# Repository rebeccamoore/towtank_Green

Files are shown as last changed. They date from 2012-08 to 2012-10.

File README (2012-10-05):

Section 1: An Introduction

This document serves as a comprehensive instruction manual for using the large tow-tank system in Link 280 at Syracuse University.  In this document, you will find descriptions of hardware and software.  It is the goal to establish this using some type of revision software.  The original document was maintained on github @ github.com/johndannenhoffer.

1.1: Document use

This document serves as a simple instruction manual for using the large tow-tank system in Link 280 at Syracuse University.  This was originally prepared by John Dannenhoffer IV.  To make changes, please indicate your name and contact information in the authors list (below) and specify which sections you contributed (and at what time these contributions were made).  If you have any questions regarding material, please direct your questions towards the most recent author of a section.  

1.1.2: Comments and plans for revision
Comments or plans for revisions will be presented using c-style comments.  This means that lines are commented using "//" and whole blocks of comments are denoted using a leading "/*" and a trailing "*/"

E.G.
This is a fake section to show commenting conventions used in this document.
//If you would like to commend a line, do so like this.

This is a list of things that will change over time.  So far we have…
foo
bar
foobar
/* this is something I plan to add later and finalize, but isn't currently finished yet
This is also something that should be continued */

1.1.3: Revision control software

By using revision control software, a document that goes through a number of changes can be maintained such that if undesirable changes are made, one can go back to previous versions.  Also, size is reduced by not having to keep archived files.  A free and easy to use software that implements revision control is Git and it's website github.com.  NOTE: To be free, an accounts material must remain open to the public.  This may be undesirable in the future.  There are two ways to use this software.  You can either download git to your local computer and manage your files (called repositories) that way or you can upload and download content through the web while logged into your account.

Branching: To change a document for your own purposes, create a branch from some node of the project.  Go to github.com to learn about this process.

Section 1.2 Authors

John Dannenhoffer IV (JFD4)
315-256-3521
johndannenhoffer@gmail.com

Summer research student for the summer of 2012.  Original author

Revision History
8/20/2012 - Created document and added sections 1,2,3, and 4 (JFD4)
//10/6/2012 - Added pictures of hardware (JFD4)

Section 1.2: Contents

This document contains a number of sections which describe different parts of the system (hardware, software, instructions,...)

1. Introduction:  Describes the use and maintenance of this document and its contents.

2. Running the tow tank:  A quick how-to guide to operating the tow tank.

3. Tow tank hardware:  The main hardware components are explained here

4. Tow tank software. The software used to run and gather data from the tow tank is described here

/* To be added later
5. PIV.  The components used for flow visualization are described here

6. Beginning Electronics for Experimentalists: This serves as a guide to electronics for experimentalists, especially those not 

7. Instrumentation for Experimentalists: A brief description of instrumentation techniques useful for the experimentalist.  This and the next section are geared towards experimentalists working in fluid mechanics

8. Actuation for Experimentalists: A description of actuation techniques useful for the experimentalist.  Microcontrollers, DC Motors, solenoids, servos, LEDs, MOSFETs and H-Bridge drivers, amplifiers, and much more will be discussed.  This section, along with sections 5 can serve as a guide to designing actuation system for experimental use.

9. Electronics Fabrication for Experimentalist:  This section describes experiential knowledge on different techniques to setup electronic apparatus for use in a lab setting.  Breadboarding, prototyping, soldering, and PCB (printed circuit board) production are discussed.

10. Purchasing: Specific vendors and purchasing techniques for everything electronic are discussed here.  Take this section with a grain of salt, as the electronics landscape changes very quickly.

*/

Section 2: Running the tow tank

This section describes the basics of running the tow tank.

2.1: What is needed to run the tow tank?

To run the tow tank, the following is needed to run the tow tank.

-Arduino hardware.  An Arduino is a micro controller development board which is used for quick prototyping of embedded systems.  Digital and analog signals from hardware can interfaced with software written in an easy to write c-based language.  The Arduino board (there are a number of generations of boards with slight differences) has header pin outputs for almost all of its pins.  This allows the user to connect peripherals to the Arduino such a digital signals, analog signals, serial signals, power,…  The board that was used for the first generation of the tow tank was the Arduino Uno.  Also, because there is a large Arduino community, a number of open source hardware and software tools have been developed.  Supplementary hardware which are attached on top of an Arduino are called shields.  These can serve many purposes.  Also, a number of software libraries have been developed to do various things within software, such as numerical calculations, interfacing with certain hardware,…  This project uses one shield (below) and its corresponding library.

-Arduino Software.  This is software that is used to communicate between a computer and the micro controller development board (Arduino).  Go to http://arduino.cc/en/Main/Software to download the latests version of the software. The Arduino software contains three important things.  1) An IDE (integrated development environment) to write and compile code in. 2) Drivers to communicate with the Arduino.  This allows you to upload your code onto the board.  It also allows for serial communication. 3) A serial monitor.  This allows the user to monitor the serial communication between the Arduino hardware and the computer.  This can be used very effectively as a debugging tool.

-A power source.  You need a way to power the power electronics in the tow tank system.  An ATX power supply and breakout board is used for this purpose.

-Pololu motor driver shield.  This "shield" is used in order to allow an Arduino to switch large amounts of current on an off.  http://www.pololu.com/catalog/product/2502  .  This shield plugs into the Arduino on top (it will only fit one way).  Through the connections with the Arduino, the program running on the Arduino controls the hardware on the shield and through this hardware, can control large amounts of current.  We use this to drive the motors for the tow tank.

-Pololu motor driver shield library.  To control the motor driver shield, software needs to be written on the Arduino.  Because interfacing with the shield is not trivial, a software library has been developed to make interfacing with the shield easier.  This allows simple function calls in your code to control the shield.  Go to https://github.com/pololu/Dual-VNH5019-Motor-Shield to download the zip file (click the "zip" button next to the "http" button.   Unzip this file.  Move the folder "DualVNH5019MotorShield" to the appropriate folder which holds your Arduino libraries.  On a mac, the directory would be ~/Documents/Arduino/libraries/. On Windows, it would be My Documents\Arduino\libraries .  NOTE:  If this is the first library that you are adding, you may need to create the "libraries" folder in the appropriate place.  When you launch the Arduino application, and you click the "Sketch" drop down and "Import Libraries", you should see the DualVNH5019-Motor-Shield as an option.  If you click this, it should add the line #include "DualVNH5019-Motor-Shield.h" to the top of your code.

-(OPTIONAL) Direction control board.  To prevent the system from causing itself harm by running the carriage into one of the sides, a control board was developed which uses 2 limit switches to limit motion.  If a limit switch is pressed, the carriage is stopped from moving in the direction of that limit switch, but can still move in the opposite direction.  See section 3.2.5 for more information on this.

2.2.1: Steps to run the tow tank w/o direction control.

Below are step by step instructions for setting up and running the tow tank.

1) Power source.  Make sure the power source is working.  Plug the 24-pin connector from the ATX power supply into the distribution board (the header is polarized).  Plug the power supply into a wall outlet and turn it on.  The fan should turn on.  NOTE: If you are using a first generation power distribution board (REV 1.0), you will need to solder together the green wire with one of the black wires.  /*This is addressed in later revisions of the boards.*/

2) Check power.  If the fan turns on, check the voltage levels of each of the outputs.  The power supply will output 4 different levels: Ground (GND), 3.3 volts (3V3), 5 volts (5V), and 12 volts (12V).  Using a multimeter in voltage mode, press the black probe to any exposed metal on the ground rail (lines denote which terminal blocks (green things) and barrier strips (black things) belong to which rail).  I suggest pressing the black probe to one of the screws in a ground (GND) terminal block.  Then take the red probe and connect it to the different rails.  The meter should read out approximately 3.3, 5.0 and 12.0 volts.  The board allows for higher voltages to be achieved by "stacking."  Refer to Section 3.2.4 for more information of this.

3) If the power is working (the fan turns on and the voltage levels seems to be correct), connect power to the motor driver shield.  To do this, connect the 12V on the power distro to the VIN of the motor driver shield and the GND to the GND.  Do this using a wire with stripped ends and the terminal blocks.  A blue LED should turn on.

4) Connect the motor to channel 1 of the motor driver shield.  Connect the output of the motor (the gray cable) to a barrier strip.  The gray cable has two spade terminal outputs.  Connect these to the long barrier strip on different strips (not across from each other).  A barrier strip connects the two connections in the same row.  From the barrier strip, connect the motor to the motor shield using a cable with a spade terminal on one end and a stripped wire on the other end.  The positive motor connection (red) should be connected to the M1A terminal connection.  The negative motor connection (black) should be connected to the M1B terminal connection.

NOTE: Using "beep" mode on the multimeter checks to see if connections are made.  The multimeter will emit a beep if a short is detected between the two probes.  This is extremely useful for checking to see if connections are securely made.

Use the multimeter to check that the positive terminal of the motor is connected to the M1A terminal and the negative terminal of the motor is connected to the M1B terminal.

IMPORTANT NOTE: IN BEGINNING TESTING, IT IS IMPORTANT TO MAKE SURE THAT THE SYSTEM DOESN'T BREAK ITSELF.  THIS MEANS THAT YOU SHOULD HAVE YOUR HAND ON THE POWER SUPPLY SWITCH DURING TESTING AND IF THE CARRIAGE APPROACHES A SIDE, TURN OFF THE POWER.  THIS IS ADDRESSED LATER WITH THE USE OF DIRECTION LIMITING CIRCUITS AND LIMIT SWITCHES, BUT UNTIL THOSE ARE PUT IN THE SYSTEM, PROCEED WITH CAUTION.

5) Test the motor.  Open the sketch (programs in Arduino are called sketches) called demo.pde (could be called demo.ino based on your version of the Arduino software downloaded).  This is in the pololu library zip file.  Connect the Arduino to the computer via USB cable (a light should go on on the Arduino) and click the upload button in the Arduino IDE (any compiling errors should be trivial and easily addressable).

6) "Plug" the shield into the Arduino.  This should fit only one way.

7) When the sketch is done uploading to the board (the yellow RX LED will flash while code is being uploaded onto the board), the system should start moving in the manner implemented in demo.pde.  The default (if you don't change any of the code) is to go one direction for ~1 second, speeding up along the way.  Then slow down for ~1 second to 0.  Then do the same thing in the opposite direction.  The motor should then stop for ~4 seconds.  This will then repeat.

2.2.2 Steps for running the tow tank w/ direction control:

Once the operation of the system is verified w/o direction control, implement the direction control.  This uses the direction control boards (small ~5cmx~5cm boards with 2 relays and other components) and 2 limit switches.

The steps for doing this are basically the same, but with 1 difference.  The motor must be put in series with the direction control circuit.  The workings of this control circuit are described in section 3.2.? but the basic idea is that if a limit switch is depressed, the motor can not move in a direction that would damage the system.  

To do this, take the connection between M1A and the barrier strip and "insert" the direction control circuit in this connection.

The only connection that is different for this setup is the connection between M1A and the barrier strip.  The new connections should be as follows.

-The positive terminal on the barrier strip (red spade terminal) should be connected to the CON1 screw terminal on the direction control board.  
-The CON2 screw terminal should be connected to the M1A connection on the motor driver shield.  
-Connect 12V and Ground to the board's screw terminal power connections.  

The board will allow current to flow only if the connection to the limit switch is closed (connected).  The connections to the limit switches are one the 4x1 header pin on the direction control board.  The 1 and 2 pins control 1 direction and the 3 and 4 pins control the other direction.  The wiring for this connector is described in Section 3.2.5

This means that to move in both directions, both 1 and 2 as well as 3 and 4 should be shorted.  To test this (without connecting the limit switches), use some metal object to short pins 1 and 2 and pins 3 and 4 (NOTE: It is ok to short 2 and 3 as well).

One easy way to test this setup is to use some metal object and short pins 1 and 2 while running the demo program.  The carriage should move in one direction as expected, but not the other.  Then short 3 and 4 and the carriage should move in the other direction.

NOTE:  Because the direction control board uses electromechanical relays, you will hear a click when you either make or break a connection (between 1 and 2 or 3 and 4).  This is perfectly normal.  However, you should only hear one click and if you hear multiple clicks that continue, the connection between the pins to be shorted is wrong.  Placing a precision screwdriver or allan wrench in the gap is a good way to make sure that the connection is correct.

IF EVERYTHING FUNCTIONS AS EXPECTED, THE HARDWARE SHOULD ALL BE WORKING AND YOU CAN MOVE FORWARD WITH PROGRAMMING!!!

Section 3 : Tow Tank Hardware

3.1: Physical hardware

3.1.1: The tank

3.1.2: Water containment

3.2: Electronic Hardware

3.2.1: Motor

3.2.2: Motor tachometer

3.2.3: Carriage Tachometer

3.2.4: Power distribution board

3.2.5: Direction Control Board

3.2.6: Arduino

3.2.7: Pololu Motor Driver Shield

3.2.8: Level Shifter

Section 4 : Tow Tank Software

4.1: Control software

4.1.1: Arduino

4.1.2: Pololu Motor Driver Shield Library

4.1.3: Level shifter arduino library

4.1.4: Test programs

4.1.5: Serial GUI

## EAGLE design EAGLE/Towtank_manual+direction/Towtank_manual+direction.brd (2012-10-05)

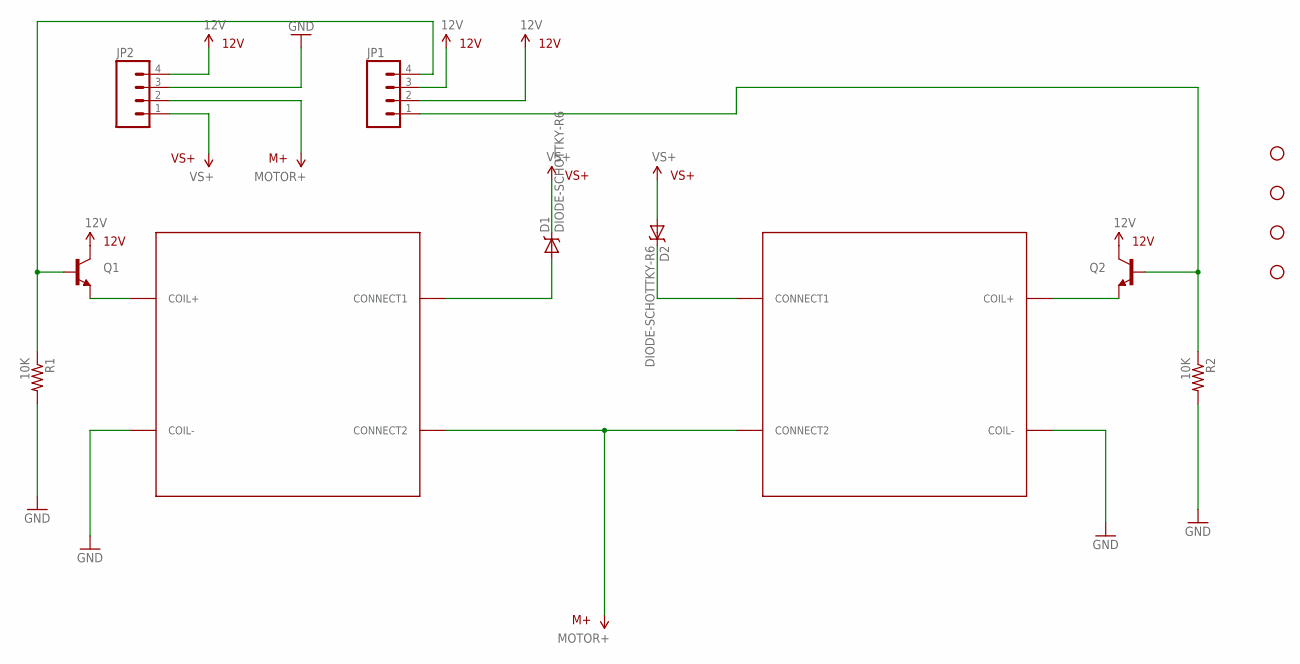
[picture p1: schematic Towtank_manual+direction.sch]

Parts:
D1, D2: DIODE-SCHOTTKY-R6; R6-AXIAL
JP1: M04LOCK_LONGPADS; 1X04_LOCK_LONGPADS
JP2: M04SCREW_LOCK; SCREWTERMINAL-3.5MM-4_LOCK
JP3, JP4, JP5, JP6: STAND-OFF
Q1, Q2: TRANSISTOR_NPNTO-92-AMMO; TO-92-AMMO
R1, R2: 10K; AXIAL-0.4
U1, U2: G5LE-1A4_SPST-NO; PC-PIN

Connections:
12V: JP1.2, JP1.3, JP2.4, Q1.3 (C), Q2.3 (C)
GND: JP2.3, R1.P$2 (2), R2.P$2 (2), U1.COIL-, U2.COIL-
MOTOR+: JP2.2, U1.CONNECT2, U2.CONNECT2
unnamed: D1.P$ANODE (ANODE), U1.CONNECT1
unnamed: D2.P$CATHODE (CATHODE), U2.CONNECT1
unnamed: JP1.4, Q1.2 (B), R1.P$1 (1)
unnamed: JP1.1, Q2.2 (B), R2.P$1 (1)
unnamed: Q1.1 (E), U1.COIL+
unnamed: Q2.1 (E), U2.COIL+
VS+: D1.P$CATHODE (CATHODE), D2.P$ANODE (ANODE), JP2.1

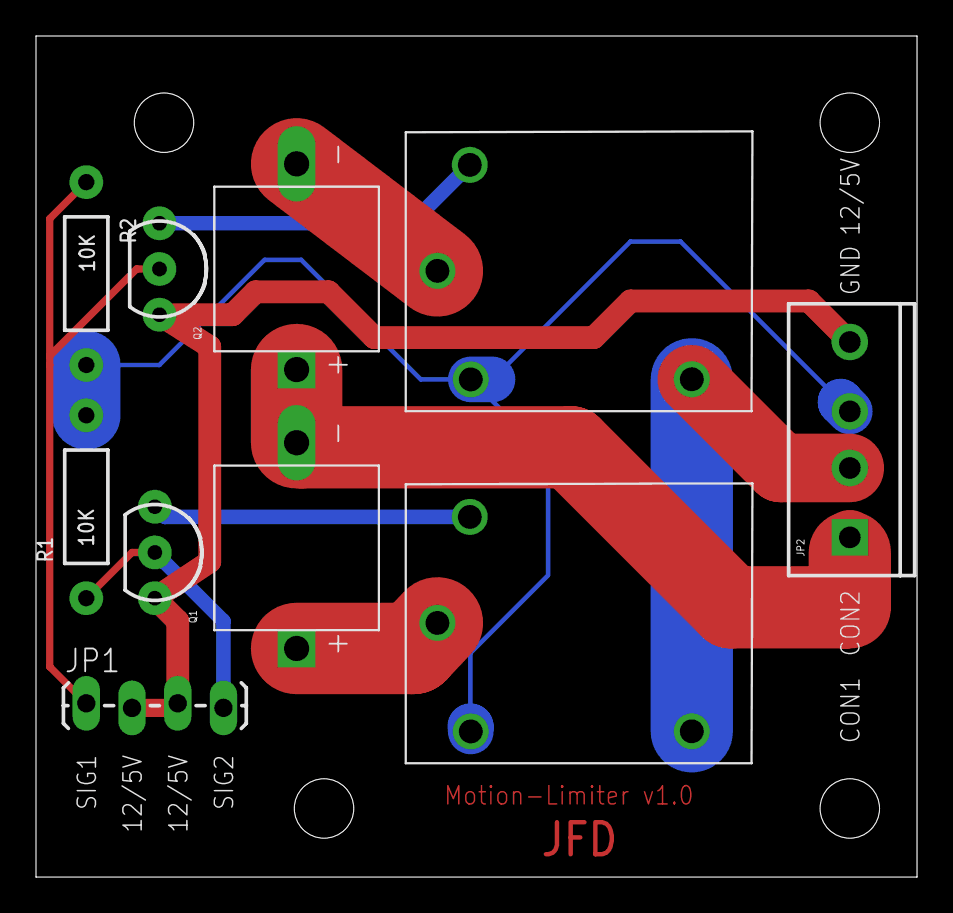
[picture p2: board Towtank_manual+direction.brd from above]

Board: 2 copper layers, 48.9 x 46.7 mm, 14 parts (0 on the bottom side), 10 nets.

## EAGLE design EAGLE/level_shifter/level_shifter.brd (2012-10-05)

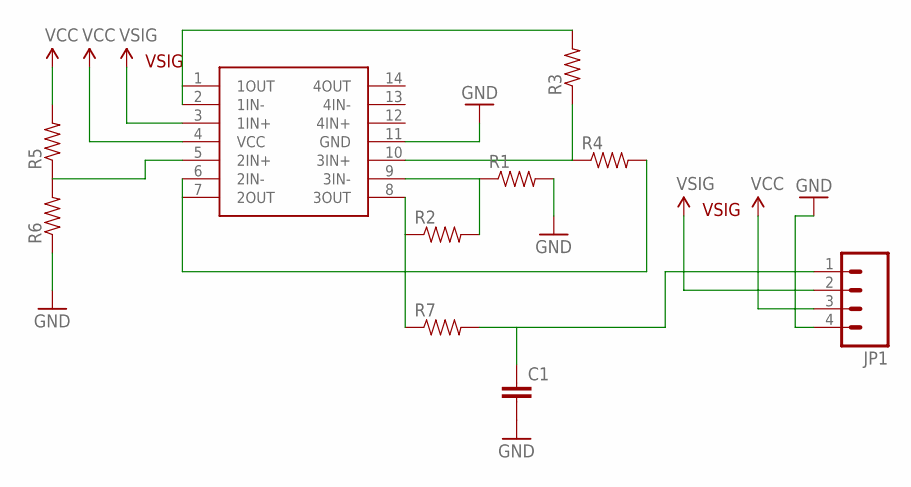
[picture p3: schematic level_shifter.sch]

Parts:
C1: CAPPTH1; CAP-PTH-5MM
JP1: M04SCREW-5MM; SCREWTERMINAL-5MM-4
R1, R2, R3, R4, R5, R6, R7: RESISTORPTH-1/4W; AXIAL-0.4
U$1: LM324DIP; DIL14

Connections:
GND: C1.2, JP1.4, R1.P$2 (2), R6.P$1 (1), U$1.11 (GND)
unnamed: R3.P$2 (2), U$1.1 (1OUT), U$1.2 (1IN-)
unnamed: C1.1, JP1.1, R7.P$2 (2)
unnamed: R4.P$2 (2), U$1.6 (2IN-), U$1.7 (2OUT)
unnamed: R3.P$1 (1), R4.P$1 (1), U$1.10 (3IN+)
unnamed: R5.P$1 (1), R6.P$2 (2), U$1.5 (2IN+)
unnamed: R1.P$1 (1), R2.P$2 (2), U$1.9 (3IN-)
unnamed: R2.P$1 (1), R7.P$1 (1), U$1.8 (3OUT)
VCC: JP1.3, R5.P$2 (2), U$1.4 (VCC)
VSIG: JP1.2, U$1.3 (1IN+)

Board: 2 copper layers, 10 parts (0 on the bottom side), 10 nets, no tracks yet.

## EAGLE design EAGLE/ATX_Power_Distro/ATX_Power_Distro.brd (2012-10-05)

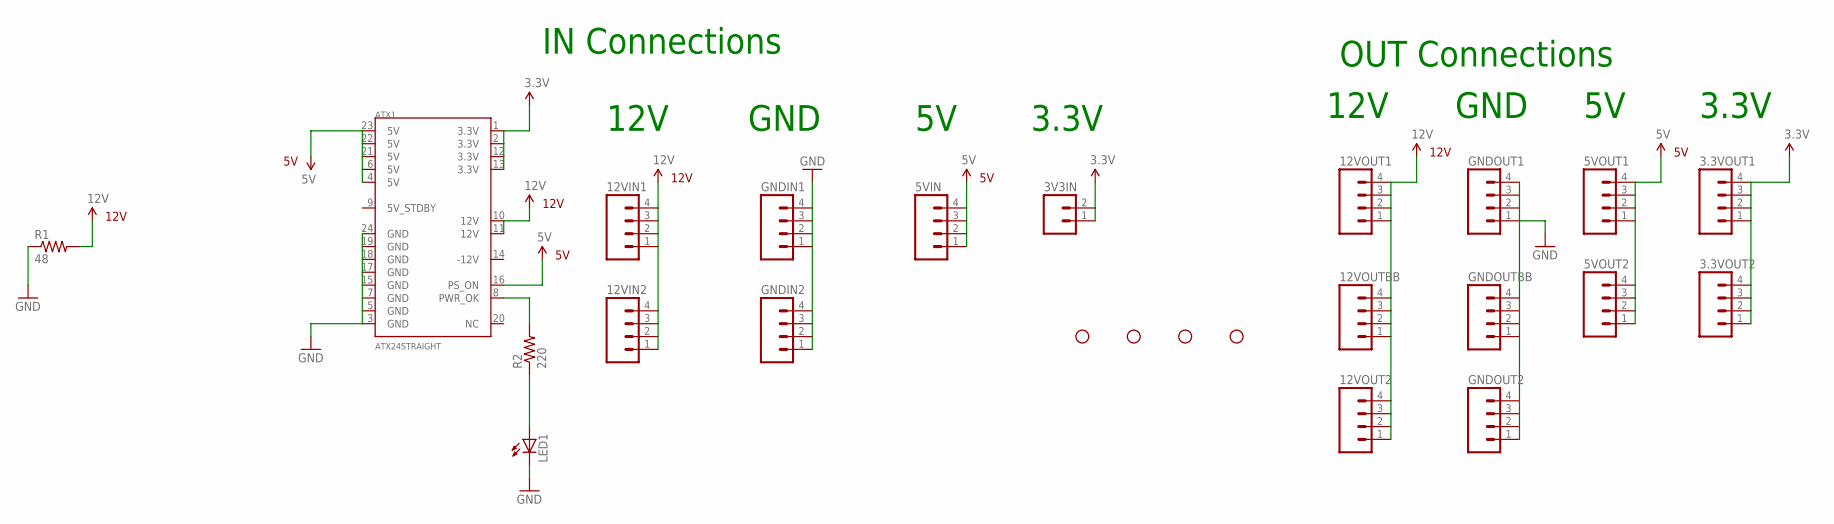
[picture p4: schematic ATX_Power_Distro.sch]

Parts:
3.3VOUT1, 3.3VOUT2, 5VIN, 5VOUT1, 5VOUT2, 12VIN1, 12VIN2, 12VOUT1, 12VOUT2: M04SCREW-5MM; SCREWTERMINAL-5MM-4
3V3IN: M025MM; SCREWTERMINAL-5MM-2
12VOUTBB: M04BARRIER_BLOCK_0.375"; 1X04_BARRIER_BLOCK_0.375"
ATX1: ATX24STRAIGHT; ATX_24
GNDIN1, GNDIN2: M04SCREW-5MM; SCREWTERMINAL-5MM-4
GNDOUT1, GNDOUT2: M04SCREW-5MM; SCREWTERMINAL-5MM-4
GNDOUTBB: M04BARRIER_BLOCK_0.375"; 1X04_BARRIER_BLOCK_0.375"
JP1, JP2, JP3, JP4: STAND-OFF
LED1: LED1206; LED-1206
R1: 48; TO220-2PIN
R2: 220; 1206

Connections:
3.3V: 3.3VOUT1.1, 3.3VOUT1.2, 3.3VOUT1.3, 3.3VOUT1.4, 3.3VOUT2.1, 3.3VOUT2.2, 3.3VOUT2.3, 3.3VOUT2.4, 3V3IN.1, 3V3IN.2, ATX1.1 (3.3V), ATX1.2 (3.3V), ATX1.12 (3.3V), ATX1.13 (3.3V)
5V: 5VIN.1, 5VIN.2, 5VIN.3, 5VIN.4, 5VOUT1.1, 5VOUT1.2, 5VOUT1.3, 5VOUT1.4, 5VOUT2.1, 5VOUT2.2, 5VOUT2.3, 5VOUT2.4, ATX1.4 (5V), ATX1.6 (5V), ATX1.16 (PS_ON), ATX1.21 (5V), ATX1.22 (5V), ATX1.23 (5V)
12V: 12VIN1.1, 12VIN1.2, 12VIN1.3, 12VIN1.4, 12VIN2.1, 12VIN2.2, 12VIN2.3, 12VIN2.4, 12VOUT1.1, 12VOUT1.2, 12VOUT1.3, 12VOUT1.4, 12VOUT2.1, 12VOUT2.2, 12VOUT2.3, 12VOUT2.4, 12VOUTBB.1, 12VOUTBB.2, 12VOUTBB.3, 12VOUTBB.4, ATX1.10 (12V), ATX1.11 (12V), R1.2
GND: ATX1.3 (GND), ATX1.5 (GND), ATX1.7 (GND), ATX1.15 (GND), ATX1.17 (GND), ATX1.18 (GND), ATX1.19 (GND), ATX1.24 (GND), GNDIN1.1, GNDIN1.2, GNDIN1.3, GNDIN1.4, GNDIN2.1, GNDIN2.2, GNDIN2.3, GNDIN2.4, GNDOUT1.1, GNDOUT1.2, GNDOUT1.3, GNDOUT1.4, GNDOUT2.1, GNDOUT2.2, GNDOUT2.3, GNDOUT2.4, GNDOUTBB.1, GNDOUTBB.2, GNDOUTBB.3, GNDOUTBB.4, LED1.C, R1.1
unnamed: ATX1.8 (PWR_OK), R2.2
unnamed: LED1.A, R2.1

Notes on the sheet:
IN Connections
OUT Connections
12V
3.3V
GND

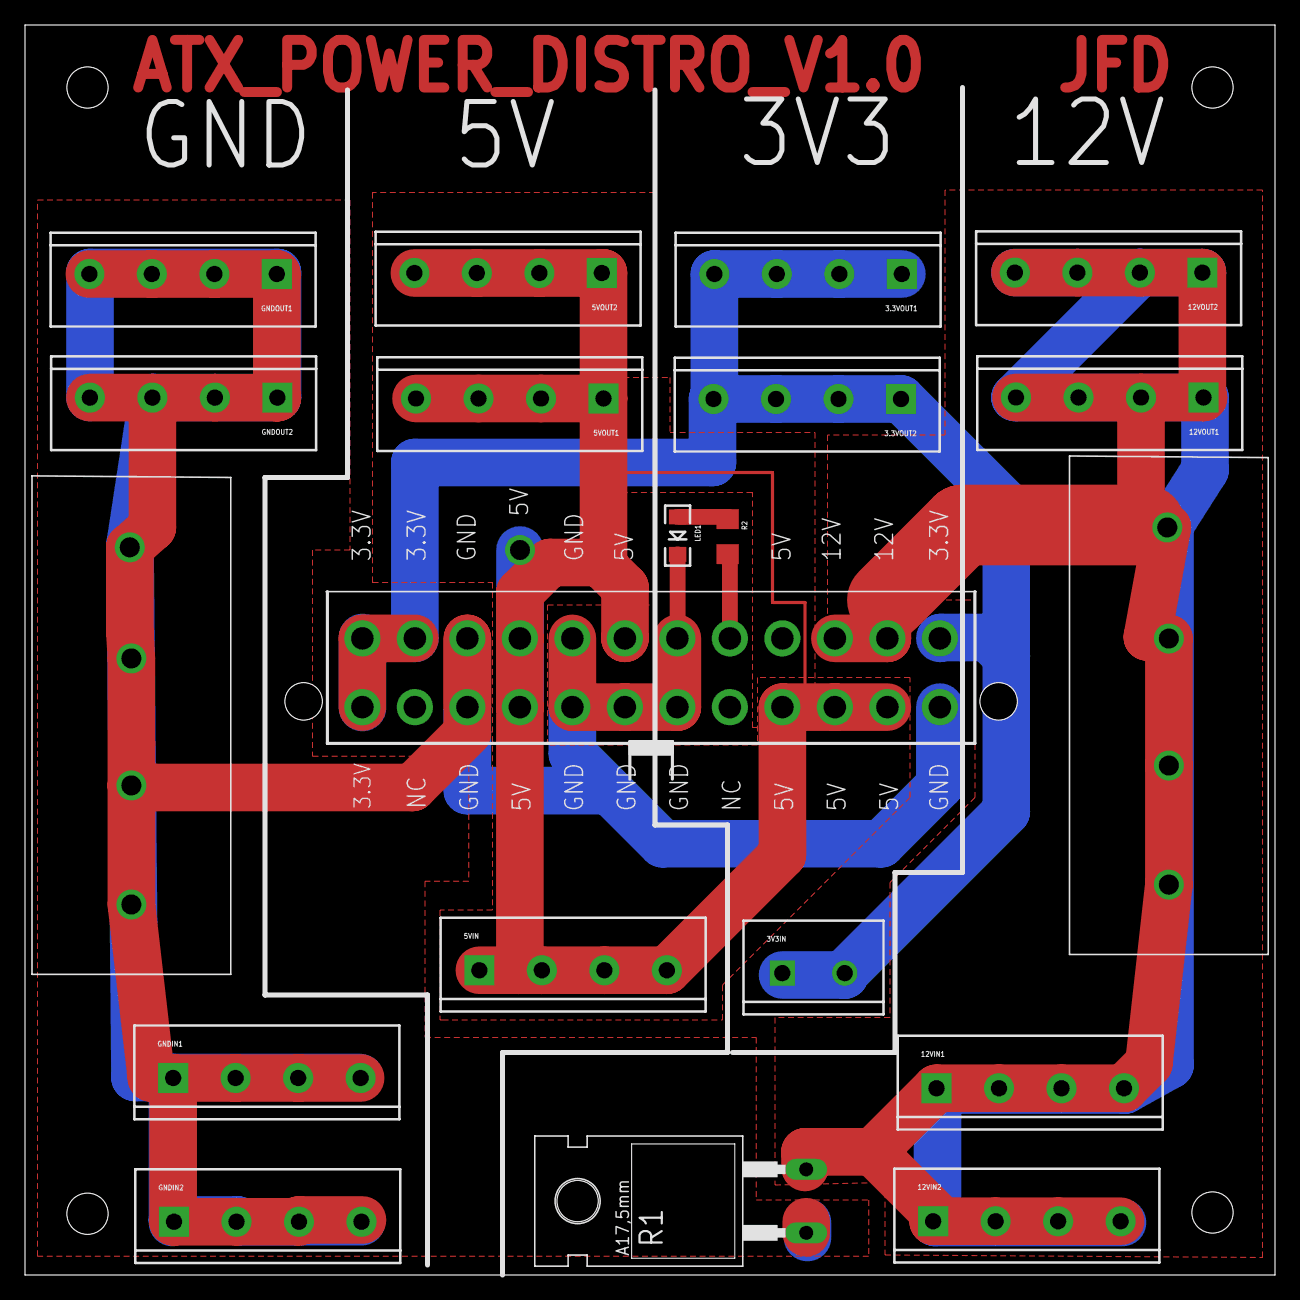
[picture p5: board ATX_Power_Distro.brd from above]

Board: 2 copper layers, 100.0 x 100.0 mm, 24 parts (0 on the bottom side), 6 nets.

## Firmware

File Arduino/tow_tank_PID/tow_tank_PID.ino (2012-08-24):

#include <DualVNH5019MotorShield.h>
double kP = 100.0;
double kD = 0.5;
double kI = 1.0;
double v;
double vD;
double vError;
double vErrorLast;
double vErrorIntegral = 0;
byte dummy = B0000000;
int incomingByte = 0;
boolean changed;

unsigned long loopStart;  //the time of the beginning of the last loop

unsigned long timeStepMicros = 5000;

unsigned long timeMicros;


double command;

DualVNH5019MotorShield md;


double getVelocity(){
  double offsetVoltage;
  double RPM;
  const double V2RPM = 0.00225;
  const double VEL2RPM = 324.676;
  double velocity;

  offsetVoltage = analogRead(4)*5.0/1024.0 - 2.5;

  RPM = (offsetVoltage*4.0)/V2RPM;

  velocity = RPM/VEL2RPM;

  return velocity;

}

void changeParameters(){
  Serial.println("IN CONSTRUCTION");

}

double changeSpeed(double vD){
  Serial.println("Press (+) to increase vD and (-) to decrease (in 0.1 in/s increments)");
  Serial.println("Press (N) to negate");
  Serial.println("Press (E) to exit");
  int incomingByte = 0;
  while(incomingByte != 69){
    if(Serial.available() > 0) {
      incomingByte = Serial.read();
    }
    if(incomingByte == 0){
    }
    else if(incomingByte == 43){
      vD += 0.1;
      Serial.print("vD = ");
      Serial.println(vD);
      incomingByte = 0;
    }
    else if(incomingByte == 45){
      vD -= 0.1;
      Serial.print("vD = ");
      Serial.println(vD);
      incomingByte = 0;
    } 
    else if(incomingByte == 78){
      vD = vD*-1.0;
      Serial.print("vD = ");
      Serial.println(vD);
      incomingByte = 0;
    }
    else if(incomingByte == 69){
      Serial.println("EXITING");
    }
    else{
      Serial.println("Not a recognized command");
      Serial.println("Press (+) to increase vD and (-) to decrease (in 0.1 in/s increments)");
      Serial.println("Press (N) to negate");
      Serial.println("Press (E) to exit");
      incomingByte = 0;
    } 
  }
  return vD;
}


void setup(){
  Serial.begin(115200);
  md.init();
  vD = 1.0;
  loopStart = micros();
}

void loop(){
  incomingByte = 0;
  vErrorIntegral = 0.0;
  Serial.print("The current desired speed is ");
  Serial.print(vD);
  Serial.println(" (in/s).");
  Serial.print("The current kP is ");
  Serial.println(kP);
  Serial.print("The current kD is ");
  Serial.println(kD);
  Serial.print("The current kI is ");
  Serial.println(kI);
  Serial.println("Press capital s (S) to start the tracking");
  Serial.println("Press capital c (C) to change speed");
  Serial.println("Press capital u (P) to update PID gains");

  while(incomingByte == 0){  
    if(Serial.available() > 0) {
      incomingByte = Serial.read();
    }
  }

  if(incomingByte == 67){
    vD = changeSpeed(vD);
  }

  else if (incomingByte == 80){
    changeParameters();
  }

  else if(incomingByte == 83){  

    loopStart = micros();

    while(incomingByte == 83){
      if(Serial.available() > 0) {
        incomingByte = Serial.read();
      }

      loopStart += timeStepMicros;

      v = getVelocity();
      vError = vD - v;

      command = kP*(vError) + kD*(vErrorLast - vError)/(timeStepMicros/1000000.0) + kI*vErrorIntegral;

      md.setM1Speed(command);

      //      Serial.print("V=");
      Serial.println(v);
      //      Serial.print("C=");
      //      Serial.println(command);


      vErrorLast = vError;
      vErrorIntegral += vError;

      timeMicros = micros();
      dummy = B00000000;
      if (timeMicros < (loopStart+timeStepMicros)){
        while(micros() < (loopStart + timeStepMicros)){
          //timeMicros = micros();
          dummy = B11111111;
          //delayMicroseconds(0);
        }
      }
      Serial.println(dummy);
    }
  }

  else{
    Serial.println("INCORRECT COMMAND");
  }

  md.setM1Speed(0);

}

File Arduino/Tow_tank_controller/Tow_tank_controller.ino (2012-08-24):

#include <DualVNH5019MotorShield.h>



DualVNH5019MotorShield md;
double offsetVoltage;
double RPM;
const double V2RPM = 0.00225;
const double VEL2RPM = 324.676;
double velocity;
int loopStart;

void stopIfFault()
{
  if (md.getM1Fault())
  {
    Serial.println("M1 fault");
    while(1);
  }
  if (md.getM2Fault())
  {
    Serial.println("M2 fault");
    while(1);
  }
}

double velocityControl(double desiredV, DualVNH5019MotorShield motorDriver){
  double offsetVoltage;
  double RPM;
  const double V2RPM = 0.00225;
  const double VEL2RPM = 324.676;
  double velocity;
  
  offsetVoltage = analogRead(4)*5.0/1024.0 - 2.5;
      
  RPM = (offsetVoltage*4.0)/V2RPM;

  velocity = RPM/VEL2RPM;

  if(desiredV > 0){
    if(desiredV > velocity){
      motorDriver.setM1Speed(100);

      
      Serial.print("F ");
      Serial.println(velocity);
    }
    else{
      motorDriver.setBrakes(0,0);
      Serial.print("C ");
      Serial.println(velocity);      
    }
  }
  
  
  if(desiredV < 0){
    if(desiredV < velocity){
      motorDriver.setM1Speed(-100);
      Serial.print("B ");
      Serial.println(velocity);
    }
    else{
      Serial.print("C ");
      Serial.println(velocity);
      motorDriver.setBrakes(0,0);
    }
  }
  
  
    
}

void setup()
{
  Serial.begin(115200);
  Serial.println("Dual VNH5019 Motor Shield");
  md.init();

}

void loop()
{
  for(int i = 0; i < 10; i++){
  loopStart = millis();
  while((millis() - loopStart) < 6000)
  {
    velocityControl(1.00, md);  
  }
  
  md.setBrakes(400,400);
  delay(2000);
  
  loopStart = millis();
  while((millis() - loopStart) < 6000)
  {
    velocityControl(-1.00, md);  
  }
  
  md.setBrakes(400,400);
  delay(2000);
  }
  
}

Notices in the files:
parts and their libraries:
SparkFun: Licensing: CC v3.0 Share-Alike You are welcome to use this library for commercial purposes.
